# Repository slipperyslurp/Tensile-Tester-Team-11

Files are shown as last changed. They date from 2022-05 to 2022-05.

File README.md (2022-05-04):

# Tensile-Tester-Team-11

1. Repository Contents: Aside from presentation materials and the source code, this repository contains updated design documents and a model of an unused stepper gear. Below is the parts list with links as well as special parameters needed to run the code.

2. System Parts: 

Stepper Motor -- 24-48V; 2.8A Motor -- Measures Distance 
https://www.amazon.com/dp/B00PNEPF5I/?coliid=I3ZDFR4H77MWP&colid=TA2UWTAFEFV6&psc=1&ref_=lv_ov_lig_dp_it

Motor Power Supply -- Output: 24V, 4A -> 96W -- Provides necessary power
https://www.amazon.com/dp/B08DHG7PQV/ref=sspa_dk_detail_6?pd_rd_i=B08DHG7PQV&pd_rd_w=11Mib&pf_rd_p=57cbdc41-b731-4e3d-aca7-49078b13a07b&pd_rd_wg=obhFH&pf_rd_r=GPBN1GH0QZRQ2V1AMGM1&pd_rd_r=38017391-f3c6-4365-8c83-a95110ebd574&s=electronics&spLa=ZW5jcnlwdGVkUXVhbGlmaWVyPUFMOE00R1RTM0tEWiZlbmNyeXB0ZWRJZD1BMDQ2OTgxMTJHNlpHWkFBTExCOEUmZW5jcnlwdGVkQWRJZD1BMDU1MTQxNTEySEFIS1dWQU8zVVYmd2lkZ2V0TmFtZT1zcF9kZXRhaWxfdGhlbWF0aWMmYWN0aW9uPWNsaWNrUmVkaXJlY3QmZG9Ob3RMb2dDbGljaz10cnVl&th=1

Motor Controller -- 9-42V; Model TB6600 -- Controls System
https://www.amazon.com/OUYZGIA-Chopping-Frequency-20KHZNema-Controller/dp/B08PKJG2ND/ref=asc_df_B08PKJG2ND/?tag=hyprod-20&linkCode=df0&hvadid=475715987248&hvpos=&hvnetw=g&hvrand=12524822550244063853&hvpone=&hvptwo=&hvqmt=&hvdev=c&hvdvcmdl=&hvlocint=&hvlocphy=9004728&hvtargid=pla-1207686168122&psc=1

20 kg Load Cell with Amplifier Board -- Measures Force
https://www.amazon.com/Bolsen-Tech-Portable-Electronic-Weighing/dp/B07N5KTQ2L/ref=sr_1_2_sspa?crid=3HJHNL923RH17&keywords=load+cell&qid=1648578910&sprefix=load+cell%2Caps%2C151&sr=8-2-spons&psc=1&smid=A2YPMGYKJIIDP8&spLa=ZW5jcnlwdGVkUXVhbGlmaWVyPUEyOEhGNjhBQ1BHOFowJmVuY3J5cHRlZElkPUEwNTA3NjM3MkZRWlcyU0s3NTJYWiZlbmNyeXB0ZWRBZElkPUEwNTc4MzExM0w0NktZUTRYUEpWRiZ3aWRnZXROYW1lPXNwX2F0ZiZhY3Rpb249Y2xpY2tSZWRpcmVjdCZkb05vdExvZ0NsaWNrPXRydWU=

LCD/(I2C protocol controller) -- 20x4 -- Displays Instructions
https://www.amazon.com/SunFounder-Serial-Module-Arduino-Mega2560/dp/B01GPUMP9C/ref=sr_1_6?keywords=lcd%2Bscreen%2Bwith%2Bi2c&qid=1649183651&sprefix=lcd%2Bscreen%2Bwith%2B%2Caps%2C109&sr=8-6&th=1

Switch -- 3 way momentary switch 
https://www.amazon.com/IndusTec-Wired-AMP-12V-Reversing/dp/B07TWNBCJM/ref=sr_1_5?crid=3H1CMQXBBORS&keywords=3+way+momentary+switch+arduino&qid=1649186013&sprefix=3+way+momentary+switch+arduino%2Caps%2C63&sr=8-5

Wing Nuts -- Reinforces the clamps.
Already had in person

String -- Thinner string to maximize accuracy.
Already had in person

3. Software Dependencies:

Libraries:
TimedAction - https://playground.arduino.cc/Code/TimedAction/
LiquidCrystal_I2C-1.1.2 - https://www.arduino.cc/reference/en/libraries/liquidcrystal-i2c/
HX711-master - https://www.arduino.cc/reference/en/libraries/hx711-arduino-library/

Tools:
ArduSpreadsheet - https://circuitjournal.com/arduino-serial-to-spreadsheet

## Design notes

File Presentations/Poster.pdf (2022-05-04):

# Team 11’s Tensile Tester

## Kaleb Bogardus, Mariela Monterroso, Kareem Abdeltawab, Elijah Lallemand

### Department of Electrical & Computer Engineering, University at Albany

### Problem Statement

- The University at Albany’s chemistry department, as part of their educational mission, intends to build a laboratory for undergraduate students where they can gain hands on experience testing various material properties (including tensile strength). However, due to the extremely high cost of commercial products they have been unable to equip such a laboratory.
- The goal of this project is to build an accurate, low cost, easy to use uniaxial tensile strength tester to support this educational mission.

### System Requirements

### Experimental Results

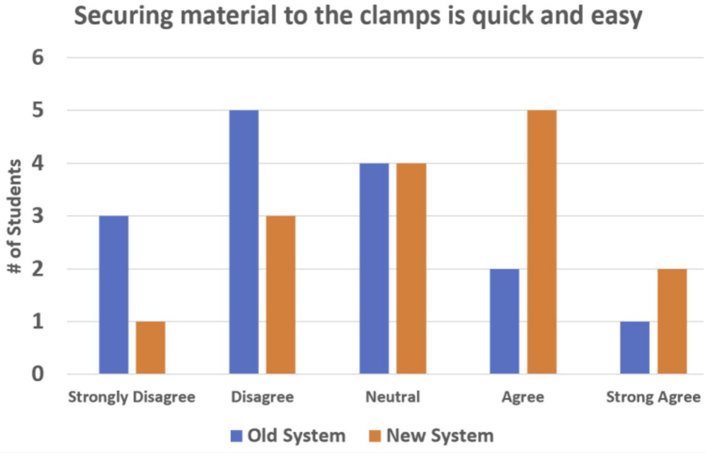
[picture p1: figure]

### Project Partners

### System Design

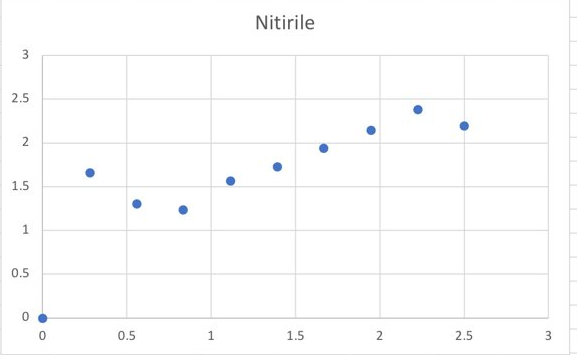
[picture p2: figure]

### System Components & Budget

Metric | Sample | Our System | Known Value | Error
Young’s Modulus | Latex | 1891.7 | 740 ± 10 kPa | 155%
… | Nitrile | 5.92 | 2.4 ± 0.2 MPa | 146.66%
Ult. Tensile Strength | Latex | 2.422 | 3.3 ± 0.1 MPa | 24%
… | Nitrile | 2.38 | 4.4 ± 0.1 MPa | 45.9%

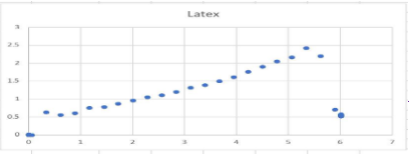
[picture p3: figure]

Part | Purpose | Cost
Stepper Motor | Measures Distance | $24
Load Cell 20kg With Amplifier Board | Measures Force | $10
String | Thinner string for system | $3
Power Supply | Provides the Necessary Power | $17
Motor Controller | Driver for the Motor | $11
Switch | Starts/Stops Rope | $9
LCD/I2C | Displays a UI for the user | $13
Wing Nuts | 8 Wing nuts reinforce clamps | $5.99
TOTAL | | $84

System Accuracy

Stress-Strain Curve
- System Accuracy: The system should be able to accurately measure the stress-strain curve, such that Young’s Modulus and Ultimate Tensile Strength can be calculated to within two significant figures.
- System Ease-of-Use: The system should be easy to calibrate and operate by undergraduate students without requiring knowledge of electronics or software programming.

Key System Features
To satisfy system requirements, we incorporated the following design modifications:
- Stepper Motor: Increase accuracy of distance
- 20kg Load Cell: Increases load capacity
- Switch: Allows start/stop of rope winding
- LCD/I2C: Allows communication between peripherals (load cell, LCD) and controller for data measurement. Physical Model

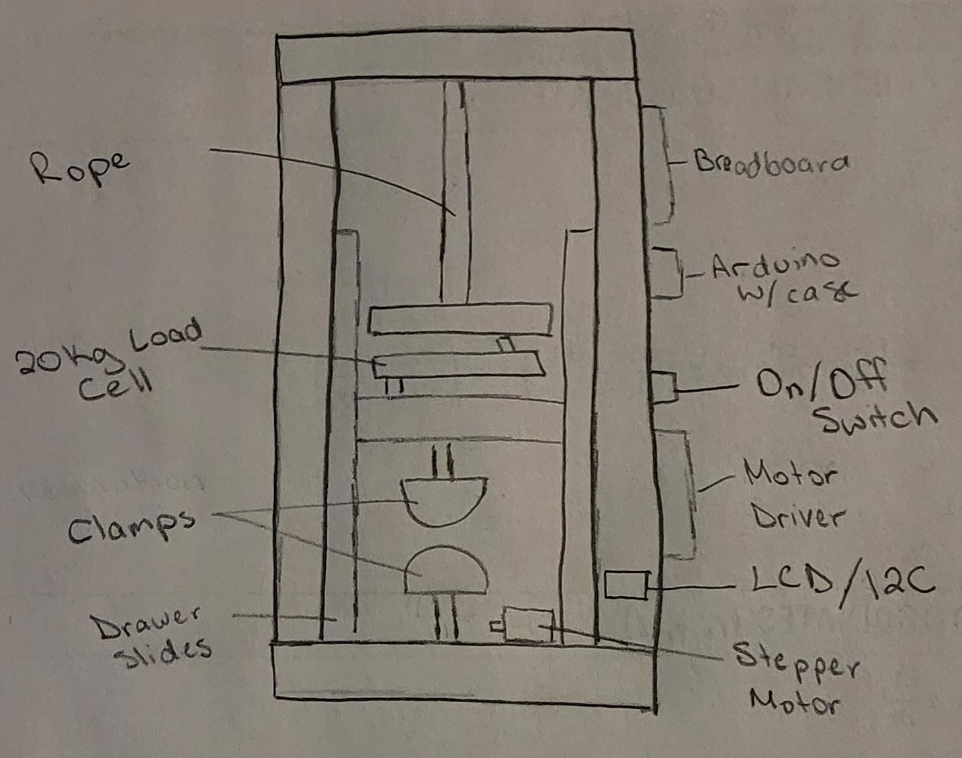
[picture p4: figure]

Circuit Schematic

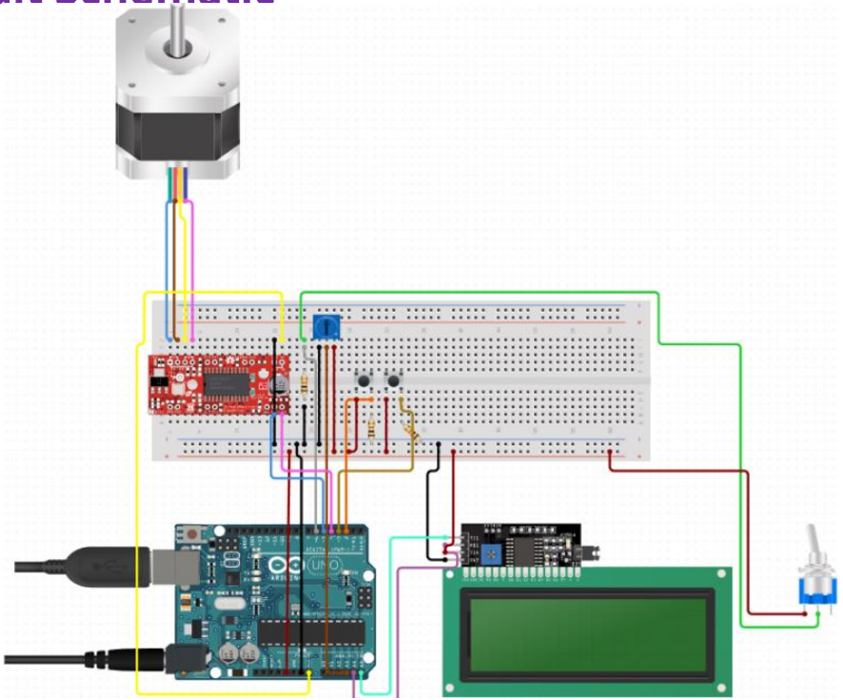
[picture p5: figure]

This system uses a micro controller to control its components. There is a driver to power and control the motor. The motor moves back and forth with a 3-way switch. The user has 3 buttons to navigate the systems menu on the LCD and to control the system.

- Special thanks for Professor Chen, Feldblyun, Yeung, and the University at Albany’s Chemistry Department for sponsoring this project.
- This project was developed in ECE442: Systems Analysis & Design in the Electrical & Computer Engineering Department.

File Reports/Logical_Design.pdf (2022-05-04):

PP-2017 V2.1

ANALYSIS & LOGICAL DESIGN | 1

# Logical Design Proposal The Salty Sea Dogs Team 11

Kaleb Bogardus, Kareem Abdeltawab, Elijah Lallemand, Mariela Monterroso

Activity Report

Abstract—This project aims to construct a cost effective tensile tester for the Chemistry Department. We have developed a design that will not only be cost effective, but also improve the base design. We plan on implementing a stepper motor, thinner string, switches/buttons, and an LCD. These improvements will yield more accurate readings and an easier to use system.

Index Terms—Uniaxial Tensiometer, System Analysis, Engineering Design

✦

### 1 BACKGROUND

T
HE Chemistry Department at UAlbany desires to conduct a laboratory where students can test the strength of materials. However, tensile testers in the market are high cost. A base tensile system has been constructed, but many improvements can be made. Gaps in the given system surmise to low ease of use and lack of accuracy. Our idea is to improve accuracy and barrier of entry by supplementing the system with a motor, switches/buttons, and a LCD screen.

### 2 SYSTEM REQUIREMENTS & CON-

STRAINTS
Figure 1 depicts the system use cases discussed in class. This system seeks to meet the stakeholders’ requirements to the best of its ability given the constraints (see constraints section
- Kaleb Bogardus,
E-mail: kwbogardus@albany.edu,
- Kareem Abdeltawab,
E-mail: kabdeltawab@albany.edu,
- Elijah Lallemand,
E-mail: elallemand@albany.edu,
- Mariela Monterroso,
E-mail: mmonterroso@albany.edu, University at Albany.

(Section 2.4)) for non-functional system requirements. The most important requirements presented by the stakeholders are as follows: Accuracy, User Friendly, and Damage Prevention. Accuracy when preforming tensile tests, user friendly design making the system straight forward to use, and damage prevention to provide feedback to the user to protect system components from damage.

### 2.1 Requirement #1 Accessibility

The switch and motor align to the principle of accessibility by making the system easiest to use. The user just has to press the switch to move the motor, which tests the sample. It collects a data trend for the material. Also, calibration is conducted via buttons in the bread board. An LCD displays instructions so the user knows what step they’re at. Finally, wing nuts were added to the clamps to make it easier to secure material within them without significantly increasing the price.

### 2.2 Requirement #2 Accuracy

The motor, switch, and new sensor all aid the accuracy of the system. The motor and switch allow measurements to be set and controlled and the new sensor has the capacity to test

Activity Report

2 | ANALYSIS & LOGICAL DESIGN

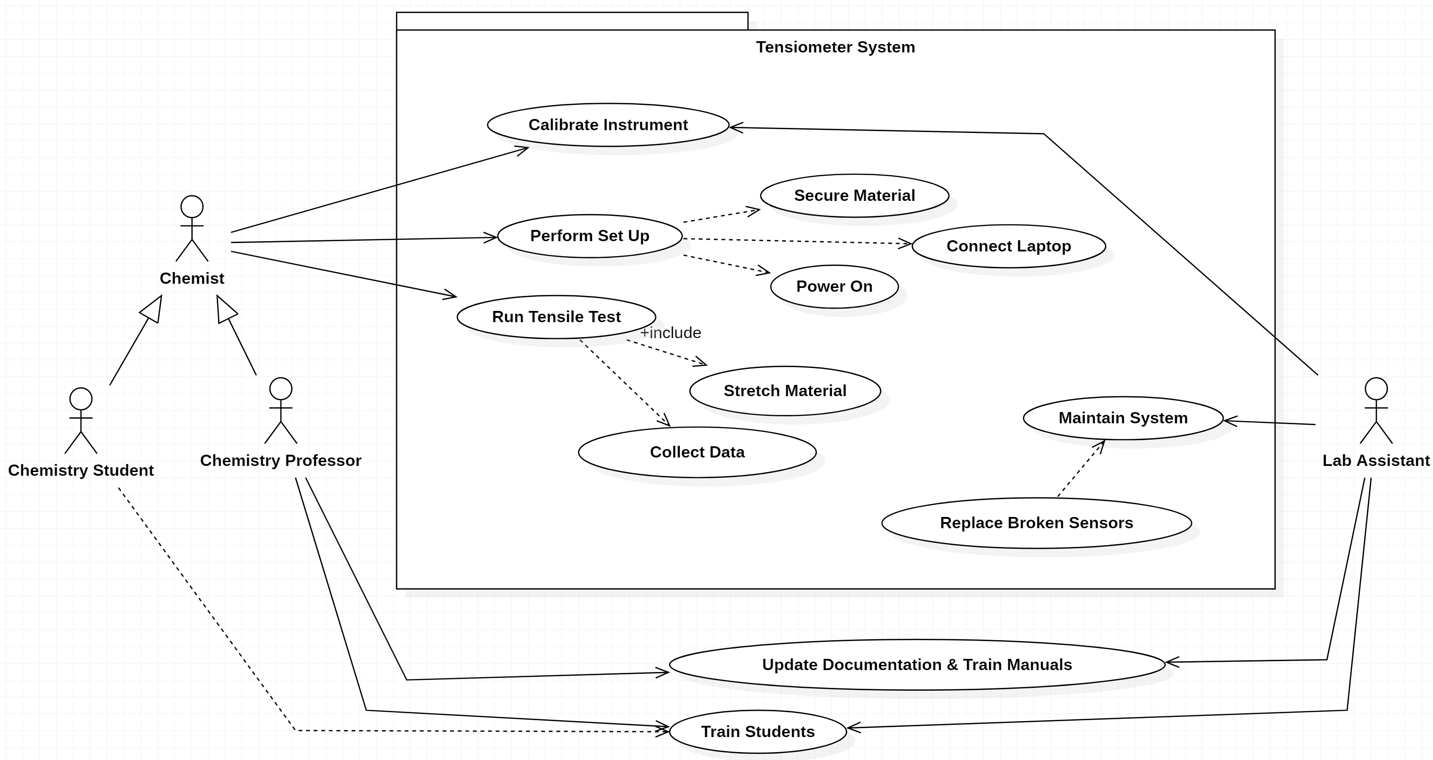
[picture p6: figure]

Figure 1. Use case model of the tensiometer system depicting system actors and the desire actions the system is required to support.

stronger material while having more accuracy
for weaker polymers.

### 2.3 Requirement #3 Durability

The stepper motor will increase the accuracy of the system as well as reduce the chance of destruction by slowly increasing the force applied and halting as soon as the user lets go of the switch.

### 2.4 Constraints

The constraints for this project are from the chemistry department. These constraints restrict the design process and limit the potential solutions. For this project, the system constraints are as follows:
- Time Constraint: Completed and read to presentation/demonstrate by April 22nd
- Budget: Cost needs to be below $150. Going over budget will require strong justification as to the value added from the cost overrun.
- Replication: Relatively straight-forward process to replicate the work, such that we can build out a lab of identical tensiometers.
- Accessibility of Parts: Parts need to be readily accessible, ship quickly (not on back order) and available from common part suppliers (e.g., Digikey, Mouser, Adafruit, SparkFun, Amazon). Avoiding parts that are difficult to source.
- Safety: System must be safe to operate without significant training or supervision

### 3 LOGICAL DESIGN

Figure 2 shown above includes a hand drawn sketch of an improved system. It includes a new load sensor that can handle more load, and a switch + motor that can apply a controlled force. The LCD will also display instructions. The clamps are also improved by using wing nuts, which makes it easier for the user to open and close them when inputting the material that is to be tested.

### 3.1 Design Justification

This design was chosen to improve the accuracy and stability of our tensiometer. A new

PP-2017 V2.1

SURNAME et al. | 3

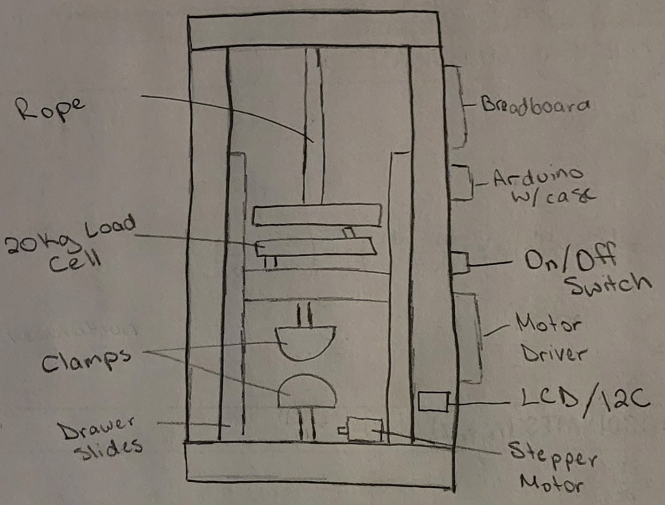
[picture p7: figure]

Figure 2. Here is a hand drawn sketch of the system with ideas for improvement.

load sensor is added to handle more weight and wing nuts are added to the clamps to make it easier for the user to add in the material that is to be tested. A switch + stepper motor are also added to apply a more consistent force.

REFERENCES

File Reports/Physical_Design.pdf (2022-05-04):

PP-2017 V2.1

PHYSICAL DESIGN | 1

# Physical Design Proposal The Salty Sea Dogs Team #11

Kaleb Bogardus, Kareem Abdeltawab, Elijah Lallemand, Mariela Monterroso

Activity Report

✦

### 1 PROPOSED SOLUTION

Various steps will be taken to improve the system’s precision and ease of use. To improve the existing system, a step motor will replace the ultrasonic range sensor in order to improve the accuracy of the distance and control the speed of the stretch in the material. The motor will be turned into a known and controlled amount of degrees at a time and this data calculate the change in distance of the rope. To further accommodate this, the rope will be replaces with a thinner string so layering does not compromise the accuracy as much. The load cell will be replaces with a 20 kg cell so stronger materials can be tested and so readings will be more accurate when the material is about to break. An LCD and buttons will be installed for ease of use. The buttons will control the motor and calibration process and the LCD will display instructions as this takes place. Finally, wing nuts will be added to the given clamps to secure the material more easily without drastically increasing cost.

- Kaleb Bogardus,
E-mail: kwbogardus@albany.edu,
- Kareem Abdeltawab,
E-mail: kabdeltawab@albany.edu,
- Elijah Lallemand,
E-mail: elallemand@albany.edu,
- Mariela Monterroso,
E-mail: mmonterroso@albany.edu,University at Albany.

### 2 SYSTEM ARCHITECTURE

To start, a main problem with the original system was not having the force be a consistent factor. The new system will have the stepper motor moving at a set speed. The motor will be mounted on the bottom of the system. The string will wrapped around the motor and attached to a pulley system. When the switch is pressed on the top, the motor will move up in a set speed. When it is pressed on the bottom, the motor will move down. This results in a controlled and adjustable data collection system. In addition, we also had issues securing the material within the clamps. The clamps will have wing nuts in order to alleviate this issue while keeping costs low. Also, the LCD will be mounted to the front of the system on the top and will display instructions from the embedded system. Buttons for calibration will be on the breadboard and the driver with the switch will be mounted on the side of the system below the breadboard.

### 2.1 System Components

2.1.1 Load Cell (20kg) / HX711 Amplifier The new system utilizes a 20 kg load cell. This higher threshold will allow the user to test stronger materials and there will be greater accuracy when materials get closer to breaking.

2.1.2 Stepper Motor
The new system requires use of a stepper motor that is used in order to pull the tensile tester device. This is what will be used to control the stretching of the substance.

Activity Report

2 | PHYSICAL DESIGN

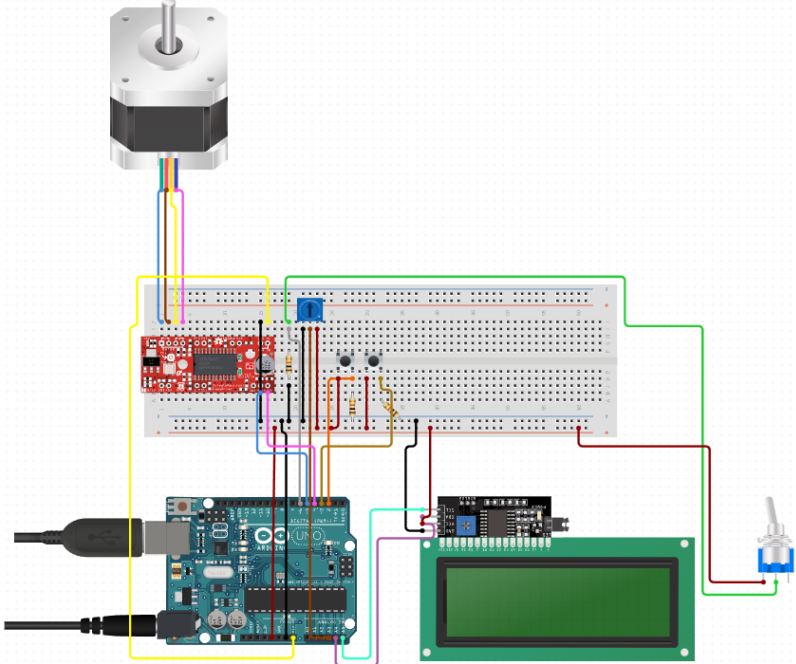
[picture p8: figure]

Figure 1. Wiring diagram of tensiometer electronics.

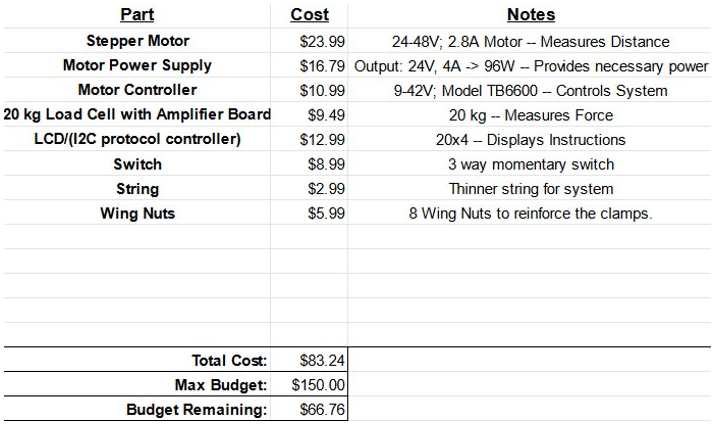
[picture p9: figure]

Figure 2. Budget of new system.

2.1.3 New String
The new system will have a different string to be pulled. This string is thinner, allowing for more minute measurements to be taken for improved accuracy.

2.1.4 Buttons
The improved system has a switch for controlling the motor. Rather than using a toggle, the motor will turn until the user lets go of the switch. Also, the modifies system has buttons in the breadboard used to trigger instructions for calibration and testing.

2.1.5 LCD
The LCD displays data and instructions so the user won’t have to look at the console in


Figure 3. The new tensiometer system implements a stepper motor, 20 kg sensor, switch, wing nuts, thinner string, and LCD.

Arduino at all times.

### 2.2 Engineering Standards

The modified system will use the I2C and UART protocols.

2.2.1 I2C Protocol
The system will be using the I2C protocol to record measurements between the load cell and the Arduino Uno. The LCD will also be using this method to communicate with the Arduino. This protocol can support multiple controls and peripherals with just two wires. The first controller to pull SDA low wins control. The address sequence is then analyzed and the instruction to record data and communicate is made. When this is acknowledged by the NACK/ACK bit, the first 8 bits are sent and data is transmitted until the receiver stops getting data or a stop condition is met.

2.2.2 UART Protocol
The connection between the laptop/embedded system and the Arduino Uno will utilize the UART protocol. It does not require a clock signal, but it requires communication purely between two devices (two lines support two way communication) and our embedded system will have a BAUD rate established ahead

PP-2017 V2.1

SURNAME et al. | 3

of time. When the code is compiled data will
be recorded. An important thing to know is
that there is no control of when data is sent
and there is no guarantee that both sides are running at exactly the same rate.

2.2.3 Data Standards
The data will will be recorded in an Arduino Spreadsheet and can be exported either to Matlab or Excel as a .csv file.

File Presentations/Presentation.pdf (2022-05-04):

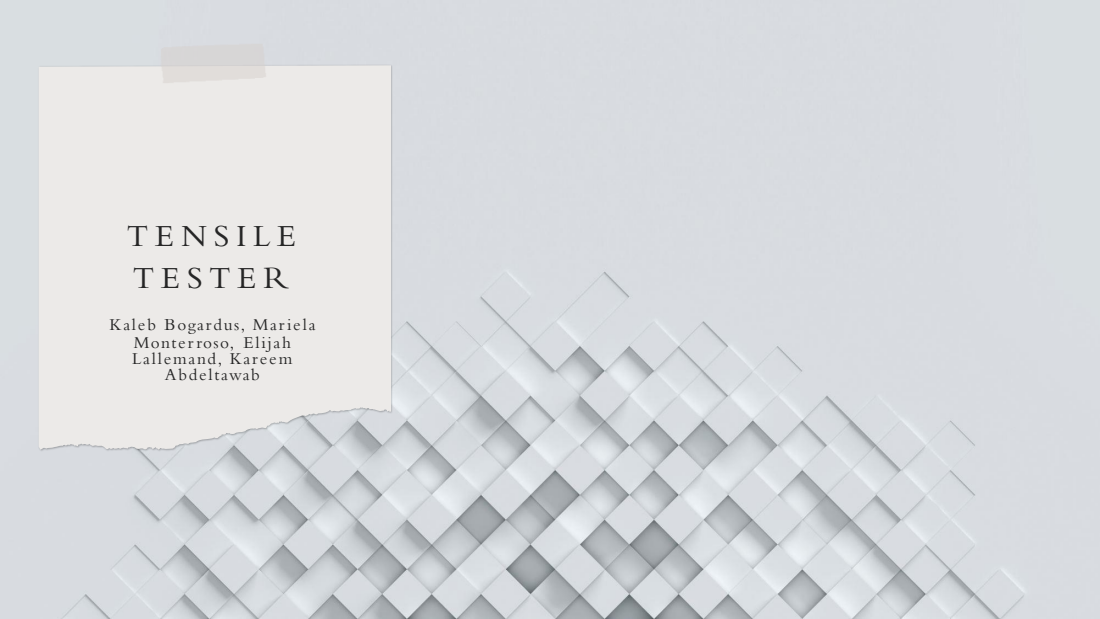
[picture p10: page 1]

Kaleb Bogardus, Mar iela
Monter roso, Elijah
Lallemand, Kareem
Abdeltawab

## G O A L S

- Accuracy + Precision
- Ease of use

## S Y S T E M D E S I G N

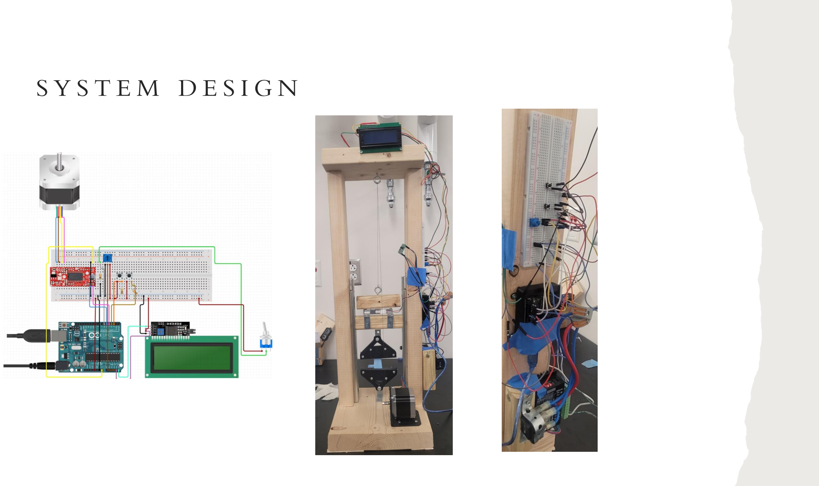
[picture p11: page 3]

## K E Y F E AT U R E S

ACCURACY:

- Stepper Motor
- 20 kg load cell
- Thinner string

EASE OF USE:

- LCD
- Wing nuts
- Switch

## S T E P P E R M O T O R

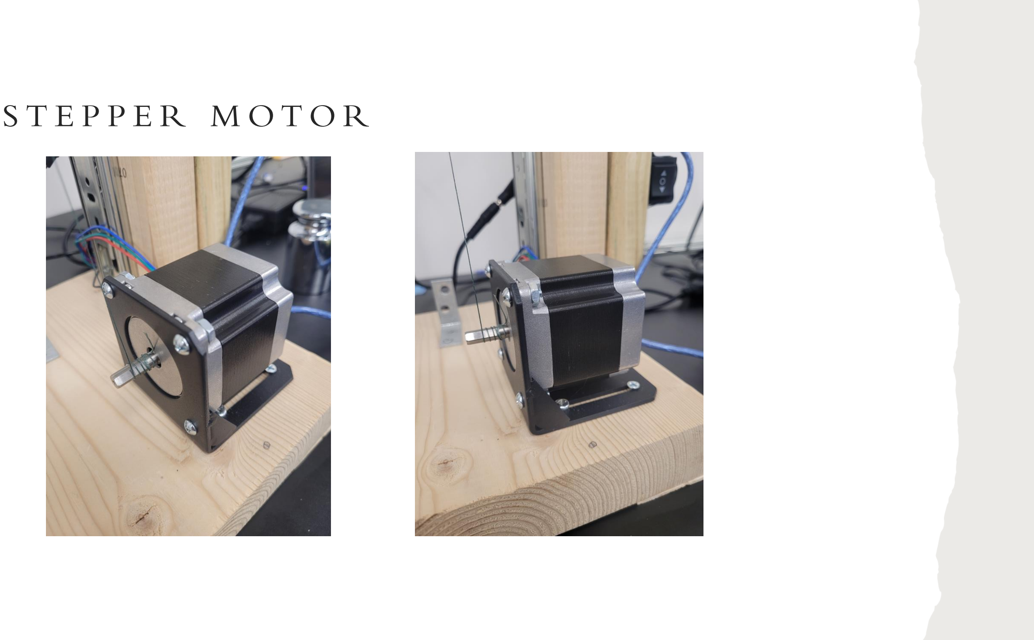
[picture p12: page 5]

## L C D S C R E E N - C A L I B R AT I O N

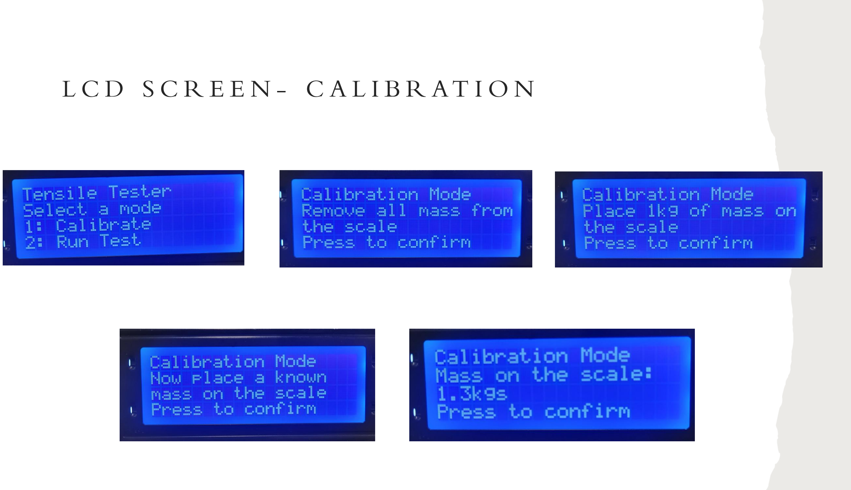
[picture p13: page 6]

## L C D S C R E E N - T E S T I N G

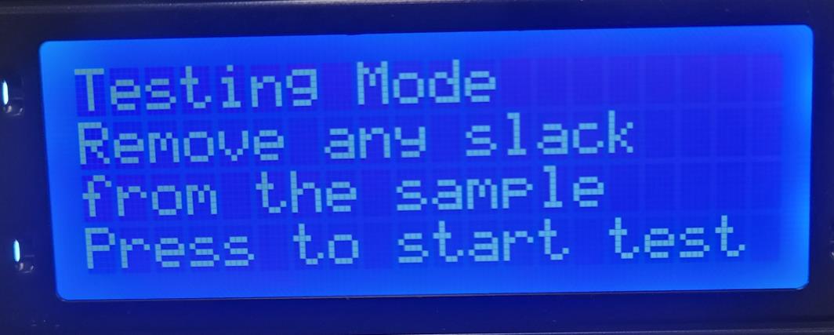
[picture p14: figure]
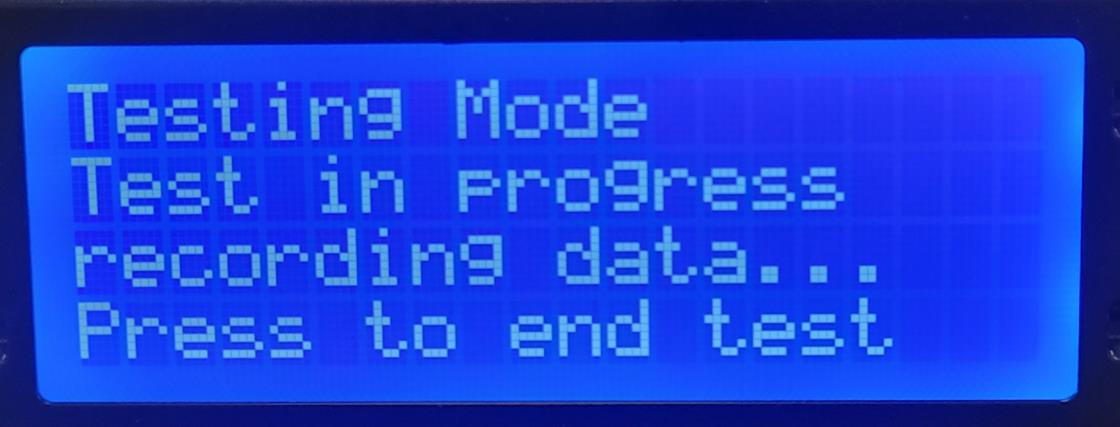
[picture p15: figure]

## S W I T C H

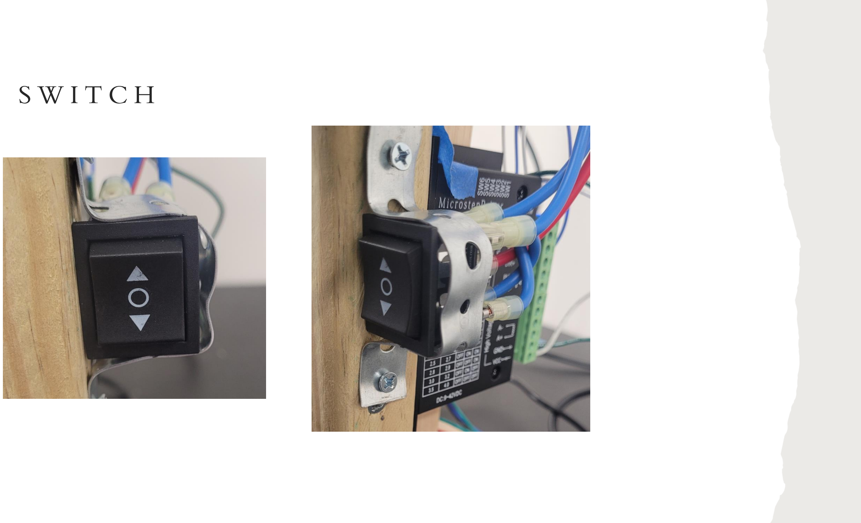
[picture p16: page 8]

## C O S T

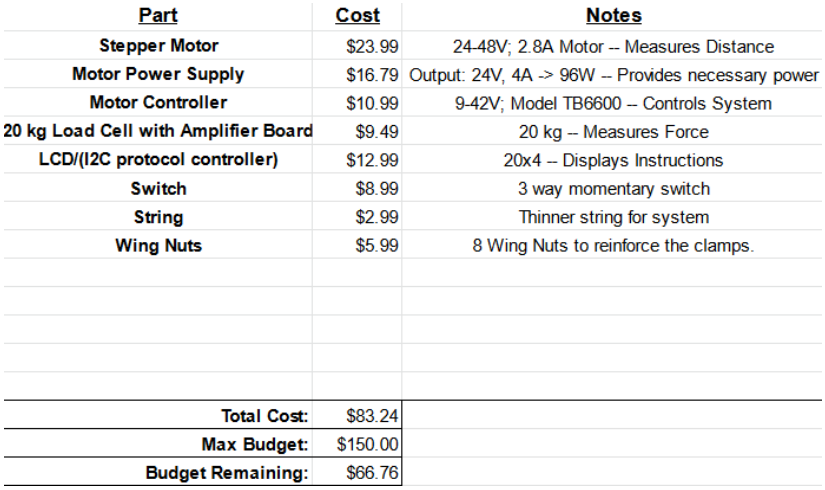
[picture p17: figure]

## R E S U LT S

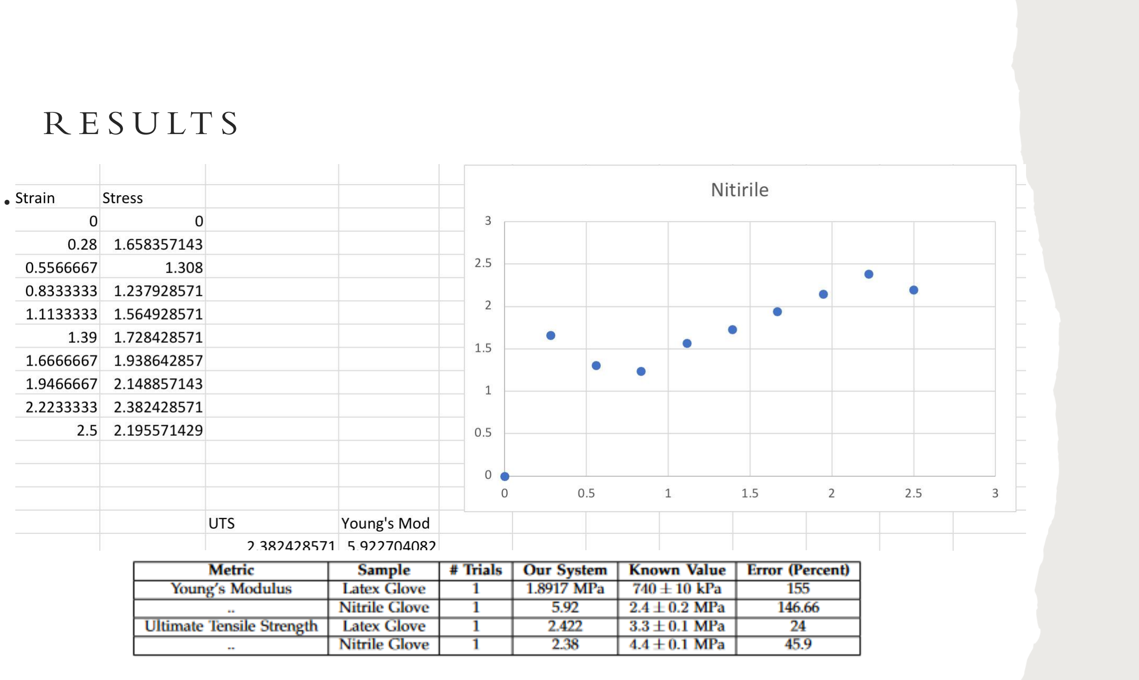
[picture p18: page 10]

•

## R E S U LT S

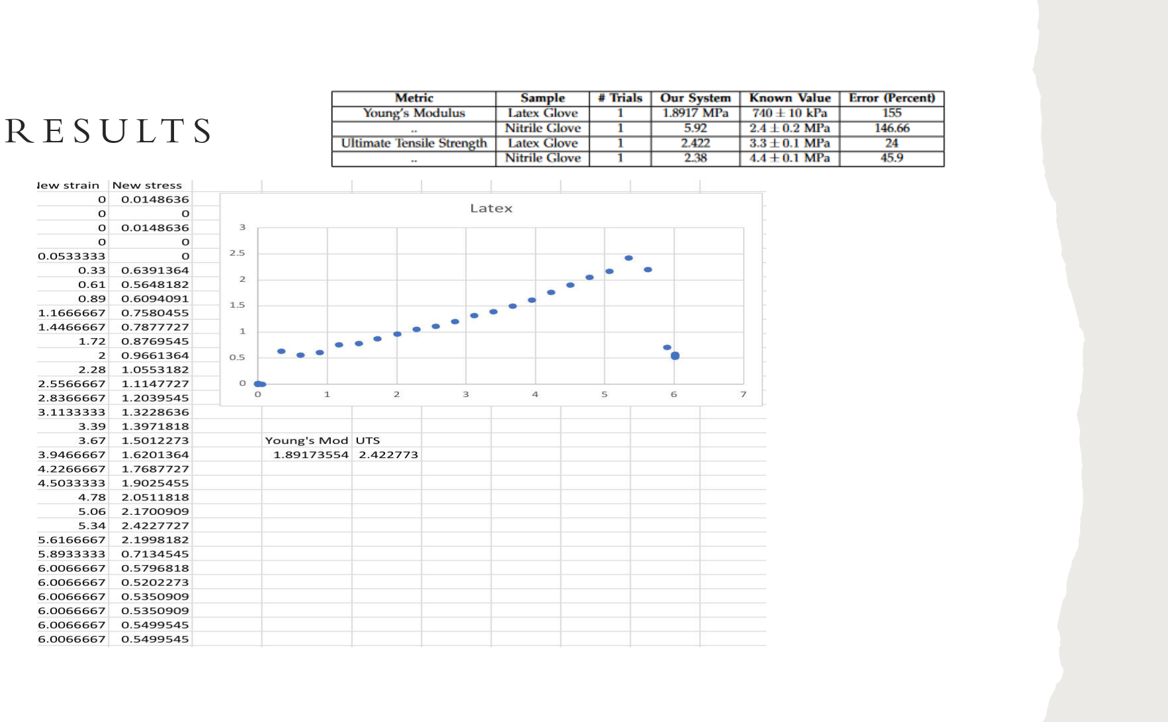
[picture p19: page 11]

One explanation for higher inaccuracy of the Young’s Modulus compared to our Ultimate Tensile Strength results is the lack of linear data points in the beginning of both curves, which is what we used to calculate

## I M P RO V E M E N T S

- New clamps
- More testing
- Rails
- Clean wiring

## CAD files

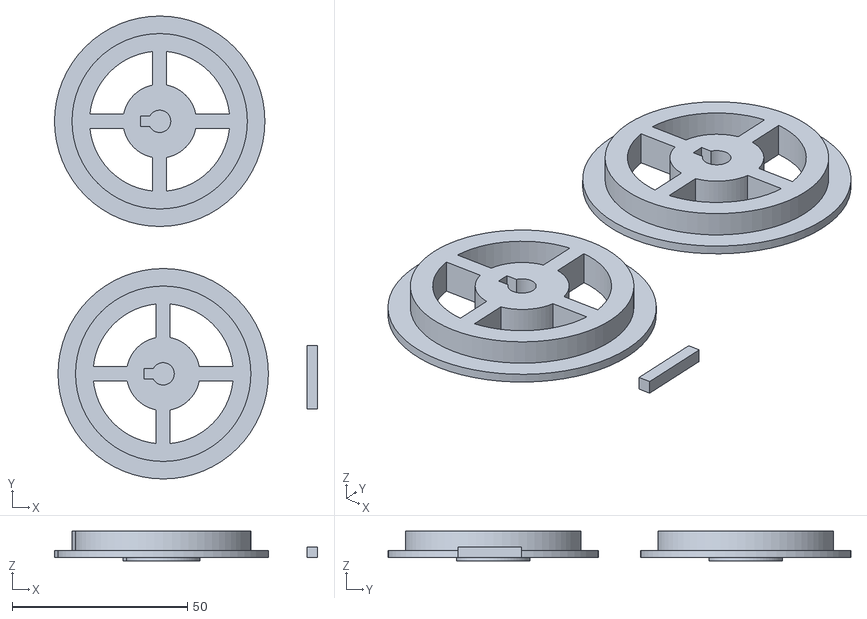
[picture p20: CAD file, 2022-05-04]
Misc/NOT_USED_stepper_motor_gear.stl
75.0 x 132.0 x 8.50

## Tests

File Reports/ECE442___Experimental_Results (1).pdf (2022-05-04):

PP-2017 V2.1

EXPERIMENTAL DESIGN | 1

# Team 11 (Experimental Results)

Kaleb Bogardus, Mariela Monterroso, Elijah Lallemand, Kareem Abdeltawab

Activity Report

✦

### 1 RESEARCH QUESTION

The primary goal to improve our uniaxial tensiometer system is to increase system accuracy by adding a stepper motor to obtain an accurate distance. To demonstrate the accuracy of our system, we tested our system on two different types of material (latex and nitrile) and compared the values of Young’s modulus and ultimate tensile strength computed from the stress-strain curve to known values for these materials.

### 2 EXPERIMENTAL RESULTS

1) Stress-strain curve for latex glove (See Figure 1)
2) Stress-strain curve for nitrile glove (See Figure 2).
3) Table summarizing key metrics (Young’s Modulus and Ultimate Tensile Strength) derived from stress-strain curves compared to known values from the original research paper (See Table 1).

### 3 DATA ANALYSIS

Our Ultimate Tensile Strength measurements were a big improvement over the base system.

- Kaleb Bogardus.
E-mail: kwbogardus@albany.edu,
- Mariela Monterroso.
E-mail: mmonterroso@albany.edu,
- Elijah Lallemand.
E-mail: elallemand@albany.edu,
- Kareem Abdeltawab.
E-mail: kabdeltawab@albany.edu,
Electrical & Computer Engineering, University at Albany.

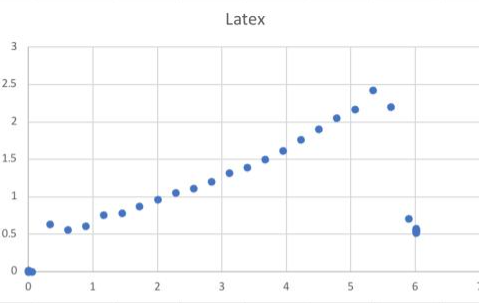
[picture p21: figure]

Figure 1. Stress-strain curve derived from our system for Latex glove sample

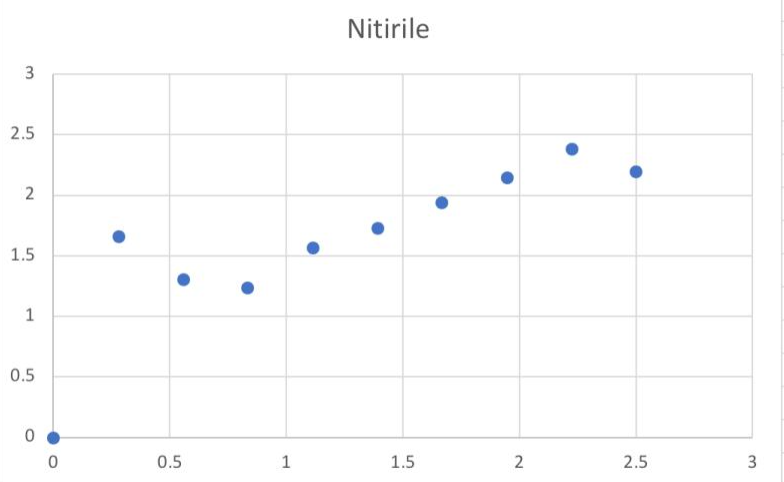
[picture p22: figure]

Figure 2. Stress-strain curve derived from our system for nitrile glove sample

Activity Report

2 | EXPERIMENTAL DESIGN
Metric | Sample | # Trials | Our System | Known Value | Error (Percent)
Young’s Modulus | Latex Glove | 1 | 1.8917 MPa | 740 ± 10 kPa | 155
.. | Nitrile Glove | 1 | 5.92 | 2.4 ± 0.2 MPa | 146.66
Ultimate Tensile Strength | Latex Glove | 1 | 2.422 | 3.3 ± 0.1 MPa | 24
.. | Nitrile Glove | 1 | 2.38 | 4.4 ± 0.1 MPa | 45.9
Table 1
Summary of experimental results from Trial 1

One explanation for higher inaccuracy of the Young’s Modulus compared to our Ultimate Tensile Strength results is the lack of linear data points in the beginning of both curves, which is what we used to calculate.

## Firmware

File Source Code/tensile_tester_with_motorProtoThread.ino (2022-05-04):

/*
 *  Tensile Tester - Stepper Motor & I2C LCD
 *  tensile_tester_with_motorProtoThread.ino
 *  Uses T660 Stepper Driver Unit
 *  With speed control & forward and reverse switch
 *  Team 11 Spring 2022
*/
#include "HX711.h"
#include <TimedAction.h>
#include <LiquidCrystal_I2C.h>

//initialize LCD_I2C the library with the number of interface pins
LiquidCrystal_I2C lcd(0x27, 20, 4); //I2C address 0x27, 20 column and 4 rows

// Switch pins
const int pinButton = 8; // forward
const int pinButton2 = 4;// backward

// Defining menu buttons 
const int nextButton1 = 3;   // #1 Push button
int nextButton2 = 2;     // #2 Push button

// Define motor driver pins
int driverPUL = 7;      // PUL- pin
int driverDIR = 6;      // DIR- pin
int varResistor = A0;           // Potentiometer

// Load cell pins
const int LOADCELL_DT_PIN = 9;
const int LOADCELL_SCK_PIN = 5;

// motor Variables
int pulseDelay = 500;       // Pulse Delay period
boolean userReady = false; // user Readys up
boolean setdir = false; // Set Direction
boolean stopMotor = true;

// distance calibration var
double otherCal = .00133;//, otherCalculatedDis = 0; // 4681958
//double slopeD = 766.00;
int currentSteps = 0; // keeps track of the motors current steps
int calInstructionStep = 0; // increments to move on the the next step for user
double calculatedDistance = 0;

// system mode var
boolean calibrate = false;
boolean testing = false;
boolean testingInprogress = false;
boolean menuPrinted = false; //

// load cell calibration var
double zero = 0, oneKg = 0, slope = -98748.00;// -98625.00;
HX711 scale;

// array for data
const int rows = 5, columns = 2;
double data [rows][columns];
int currentRow = 0;

double cm = 0;
double kgs = 0;

void printMenu() {
  menuPrinted = true; 
  // prints menu to LCD
  lcd.clear();
  lcd.setCursor(0,0);
  lcd.print("Tensile Tester");
  lcd.setCursor(0,1);
  lcd.print("Select a mode");
  lcd.setCursor(0,2);
  lcd.print("1: Calibrate");
  lcd.setCursor(0,3);
  lcd.print("2: Run Test");
}

void checkSwitchState() {
  int stateButton = digitalRead(pinButton); // get state of forward switch
  int stateButton2 = digitalRead(pinButton2);// get state of backward switch

  if(stateButton == 1) { // if forward
     //Serial.println("Forward");
     setdir = LOW;      // sets motor direction to low
     stopMotor = false; // Starts the motor
  } else
  if(stateButton2 == 1) { // if backward
     //Serial.println("Backward");
     setdir = HIGH;     // sets motor direction to high
     stopMotor = false; // Starts the motor
  } else
    stopMotor = true; // stops the motor if nothing on the switch is pressed
}

void motorControl() { // pulses motor
  // runs the motor if a switch is pressed
    pulseDelay = map((analogRead(varResistor)),0,1023,2000,50); // short delay value based on variable resistor
    digitalWrite(driverDIR,setdir);
    digitalWrite(driverPUL,HIGH); // sets motor to high
    //delayMicroseconds(pulseDelay);      // digitalWrite take time so it acts as a delay
    digitalWrite(driverPUL,LOW);  // sets motor to low
    delayMicroseconds(pulseDelay);        // short delay before the motor pulses again
    
    if (!setdir) // if the direction is forward the currentSteps counter increases 
      currentSteps++;
    else        // if the direction is backward the currentSteps counter decreases
      currentSteps--; 
}

void getData() {
  // distance measurement
  cm = (currentSteps * otherCal); // read in the distance
  // load measurement
  kgs = (scale.get_units()/slope); //reads in load
  // save data
    data [currentRow][0] = cm; // saves the current distance
    data [currentRow][1] = kgs; // saves the current load
    currentRow++;
}

// setting up threads
TimedAction measurementThread = TimedAction(500,getData); // (delay, method called)
TimedAction switchThread = TimedAction(300,checkSwitchState); // (delay, method called)

void nextB2() {
  
  delay(1000); // delay so only one button press is detected
  userReady = true; // tells the program the user is ready to move on
  if (!calibrate && !testing)
    testing = true;
}

void nextB1() {
  
  delay(1000); // delay so only one button press is detected
  userReady = true; // tells the program the user is ready to move on
  if (!calibrate && !testing)
    calibrate = true;
}

void setup() {

  // driver control pins
  pinMode (driverPUL, OUTPUT);
  pinMode (driverDIR, OUTPUT);
  attachInterrupt(digitalPinToInterrupt(nextButton1), nextB1, FALLING); // user hits a button to move on and next() is called
  attachInterrupt(digitalPinToInterrupt(nextButton2), nextB2, FALLING); // user hits a button to move on and next() is called

  // Switch setup
  pinMode(pinButton, INPUT);  // setup for forward switch
  pinMode(pinButton2, INPUT); // setup for backward switch
  Serial.begin(9600);

  // load cell setup
  scale.begin(LOADCELL_DT_PIN, LOADCELL_SCK_PIN);
  scale.set_scale();
  scale.tare();

  //initialize the lcd
  lcd.init();
  lcd.backlight();
  // set up the LCD's number of columns and rows: 
  lcd.begin(20, 4);
  
  printMenu(); // Print Menu to LCD
}

void loop() {
  
  switchThread.check();
  // Menu
  if (!calibrate && !testing && !menuPrinted)
    printMenu();
  
  if (calibrate) {

  //***Load Cell Calibration Section**********************************************************************
  
      if (calInstructionStep == 0) {
        lcd.clear();
        lcd.setCursor(0,0);
        lcd.print("Calibration Mode");
        lcd.setCursor(0,1);
        lcd.print("Remove all mass from");
        lcd.setCursor(0,2);
        lcd.print("the scale");
        lcd.setCursor(0,3);
        lcd.print("Press to confirm");
        Serial.println("Remove all weight from the scale");
        Serial.println("Press any button to continue");
        calInstructionStep = 1; // next button press will zero the load cell
        userReady = false;
        // wait till the user presses a button
      }

      if (calInstructionStep == 1 && userReady) {
        scale.tare(); // tare load cell
        zero = scale.get_units(12); // take zero reading of the load cell
        Serial.println("Put 1kg weight on the bracket");
        Serial.println("Press any button to continue");
        lcd.clear();
        lcd.setCursor(0,0);
        lcd.print("Calibration Mode");
        lcd.setCursor(0,1);
        lcd.print("Place 1kg of mass on");
        lcd.setCursor(0,2);
        lcd.print("the scale");
        lcd.setCursor(0,3);
        lcd.print("Press to confirm");
        userReady = false;
        calInstructionStep = 2; // next button press will measure the load cell at 1kg
      }

      if (calInstructionStep == 2 && userReady) {
        oneKg = scale.get_units(12);  // measure 1kg
        //Serial.println(oneKg); 
        slope = (oneKg - zero) / (1 - 0);
        userReady = false;
        calInstructionStep = 3; // next button press will measure an unknown load
        Serial.println("Put known weight on the scale");
        Serial.println("Press any button to continue");
        lcd.clear();
        lcd.setCursor(0,0);
        lcd.print("Calibration Mode");
        lcd.setCursor(0,1);
        lcd.print("Now place a known");
        lcd.setCursor(0,2);
        lcd.print("mass on the scale");
        lcd.setCursor(0,3);
        lcd.print("Press to confirm");
      }

      if (calInstructionStep == 3 && userReady) {
        Serial.print("weight on the scale: ");
        Serial.println((scale.get_units(5)/slope));
        lcd.clear();
        lcd.setCursor(0,0);
        lcd.print("Calibration Mode");
        lcd.setCursor(0,1);
        lcd.print("Mass on the scale:");
        lcd.setCursor(0,2);
        lcd.print((scale.get_units(5)/slope));
        lcd.setCursor(3,2);
        lcd.print("kgs");
        lcd.setCursor(0,3);
        lcd.print("Press to confirm");
        userReady = false;
        calInstructionStep = 4;
      }
      
      if (calInstructionStep == 4 && userReady) {
        calibrate = false;
        menuPrinted = false;
        userReady = false;
        calInstructionStep = 0; // resesting calibration mode
      }
  
  //***End of Load Cell Calibration Section***************************************************************
  } else

  if (testing) {
    
    if (calInstructionStep == 0 && !testingInprogress) { // prints mod
        lcd.clear();
        lcd.setCursor(0,0);
        lcd.print("Testing Mode");
        lcd.setCursor(0,1);
        lcd.print("Remove any slack");
        lcd.setCursor(0,2);
        lcd.print("from the sample");
        lcd.setCursor(0,3);
        lcd.print("Press to start test");
        calInstructionStep = 1;
        userReady = false;
      } else
      
    if (calInstructionStep == 1 && userReady) { // prints data heading and starts test
      scale.tare(); // set load to 0 kgs
      currentSteps = 0; // set distance to zero
      // prints to LCD
      lcd.clear();
      lcd.setCursor(0,0);
      lcd.print("Testing Mode");
      lcd.setCursor(0,1);
      lcd.print("Test in progress");
      lcd.setCursor(0,2);
      lcd.print("recording data...");
      lcd.setCursor(0,3);
      lcd.print("Press to end test");
      // printing headings in spreadsheet
      Serial.print("Distance (cm)");
      Serial.print("\t");
      Serial.print("Mass (kg)");
      Serial.print("\n");
      testingInprogress = true; // begin testing
      calInstructionStep = 2;
      userReady = false;
    }
    
    if (calInstructionStep == 2 && userReady) { // ends testing when a button is pressed
      calInstructionStep = 0;
      userReady = false;
      testingInprogress = false; // ending testing
      testing = false; // exiting testing
      menuPrinted = false;
    }
    
    
    if (testingInprogress) // takes measurements if testing
      measurementThread.check();
      
  }

  if(currentRow == rows) {
    // print to .csv file
    for (int j = 0; j < rows; ++j) { // loops through each set of data collected
        
      for (int i = 0; i < columns; ++i) { // loops through each distance and load collected
  
        Serial.print(data[j][i]); // prints data
        Serial.print("\t");
      }
      Serial.print("\n");
    }
    currentRow = 0;
  }
  
  if (!stopMotor) // runs motor if the switch is pressed
    motorControl();
}
